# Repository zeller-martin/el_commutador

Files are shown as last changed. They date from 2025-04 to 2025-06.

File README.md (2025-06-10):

# el_commutador

a simple design for an active coaxial commutator with SMA connectors. used for tangle-free freely-moving neuronal recordings in small animals using ulca miniscopes or neuropixels probes. this design mainly differs from the design sold in the open ephys store in the follwowing aspects:
* mechanical parts and electronic controller are separate devices and connected with a cable
* use of a hollow-shaft stepper instead of a gear system decreases mechanical complexity and size of the device
* more simplistic and lower-priced design, but without any housing

# assembling the commutator

the file 'bom.xlsx' contains all necessary components. the file 'assembly.pdf' outlines the assembly of the hardware. the total cost of all components for a single commutator is ca. 300 euros.

# running the commutator

load the script 'motor_teensy.ino' onto the teensy 4.0 using arduino software with teensyduino software. the file 'el_commutador.py' contains the function 'run_commutator' to launch a GUI instance for a commutator. for now we feed real-time head direction information into the system by reading the head orientation .csv-file as it is written by the miniscope recording software. in the future other sources of head direction data can be implemented to be fed in the GUI. manual operation is also possible.

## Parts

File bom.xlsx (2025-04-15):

Description | Manufacturer | Part # | Amount
SMA coaxial slip ring | Jinpat | LPHF-01A | 1
Hex standoff with internal and external thread, M3 x 25mm | generic |  | 4
Hex standoff with internal and external thread, M3 x 5mm | generic |  | 4
Cap screw M3 x 8mm | generic |  | 4
Washer M3 | generic |  | 4
Coaxial cable assembly, Male SMA to Female SMA 100mm | RS components | 794-2914 | 1
Hollow shaft stepper motor | Nanotec | ST4118M1804-L | 1
Pin header 4x1 for stepper connection | JST | B4B-XH-A | 1
4 pin connector for stepper connection | Molex | 26013115 | 2
2m cable for stepper connection | Molex | 2451350420 | 1
Teensy 4.0 with headers | PJRC |  | 1
TMC2208 stepper driver with leads | BIGTREETECH | BIQU-ZZB000294 | 1
100 Ohms SMD resistor (footprint 2010) | generic |  | 1
3mm LED | generic |  | 1
DC barrel jack 2.1 mm | Wuerth Electronic | 694106301002 (or similar) | 1
14 pin header socket | Molex | 90147-1114 | 2
8 pin header socket | Molex | 90147-1108 | 2
circ_cap | 3D print from this repository |  | 1
hex_cap | 3D print from this repository |  | 1
commut_plate | from this repository, send to PCB fab (e.g. Aisler in Europe) |  | 1
controller_pcb | from this repository, send to PCB fab (e.g. Aisler in Europe) |  | 1
USB A to USB micro cable | generic |  | 1
DC power adapter, 12V, 2.A | XP power | VEL24US120-EU-JA (or similar) | 1
Plexiglass plate, 5mm thick, with cutouts | this repository, ideally commission at your instituions workshop |  | 1

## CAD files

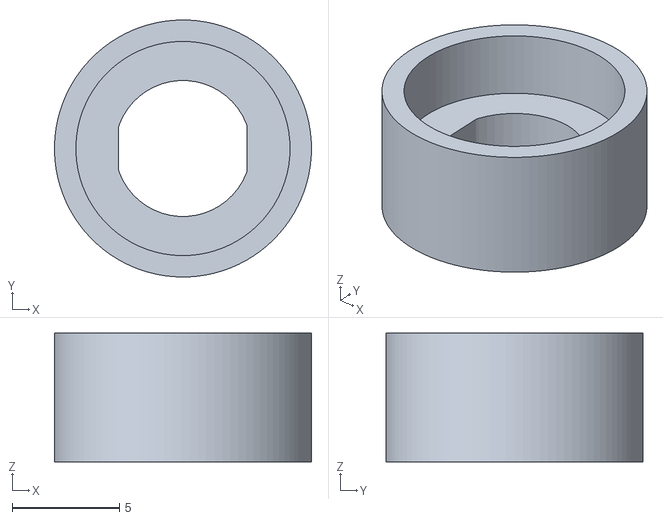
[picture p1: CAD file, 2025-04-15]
circ_cap.stl
12.0 x 12.0 x 6.00

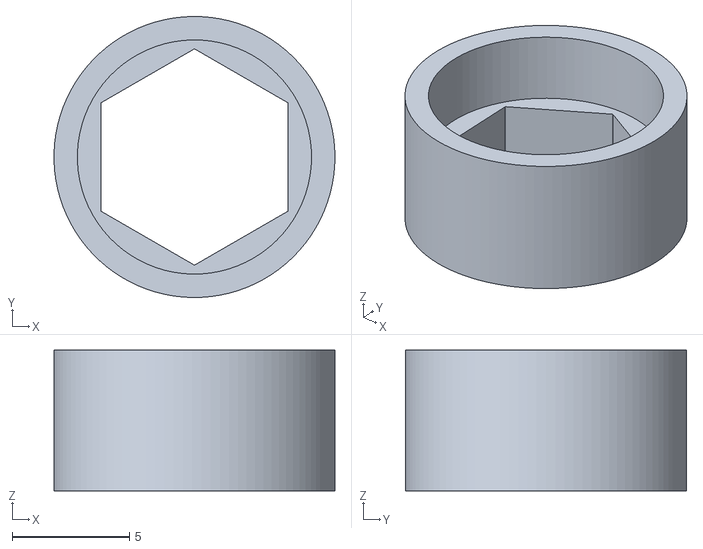
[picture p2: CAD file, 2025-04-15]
hex_cap.stl
12.0 x 12.0 x 6.00

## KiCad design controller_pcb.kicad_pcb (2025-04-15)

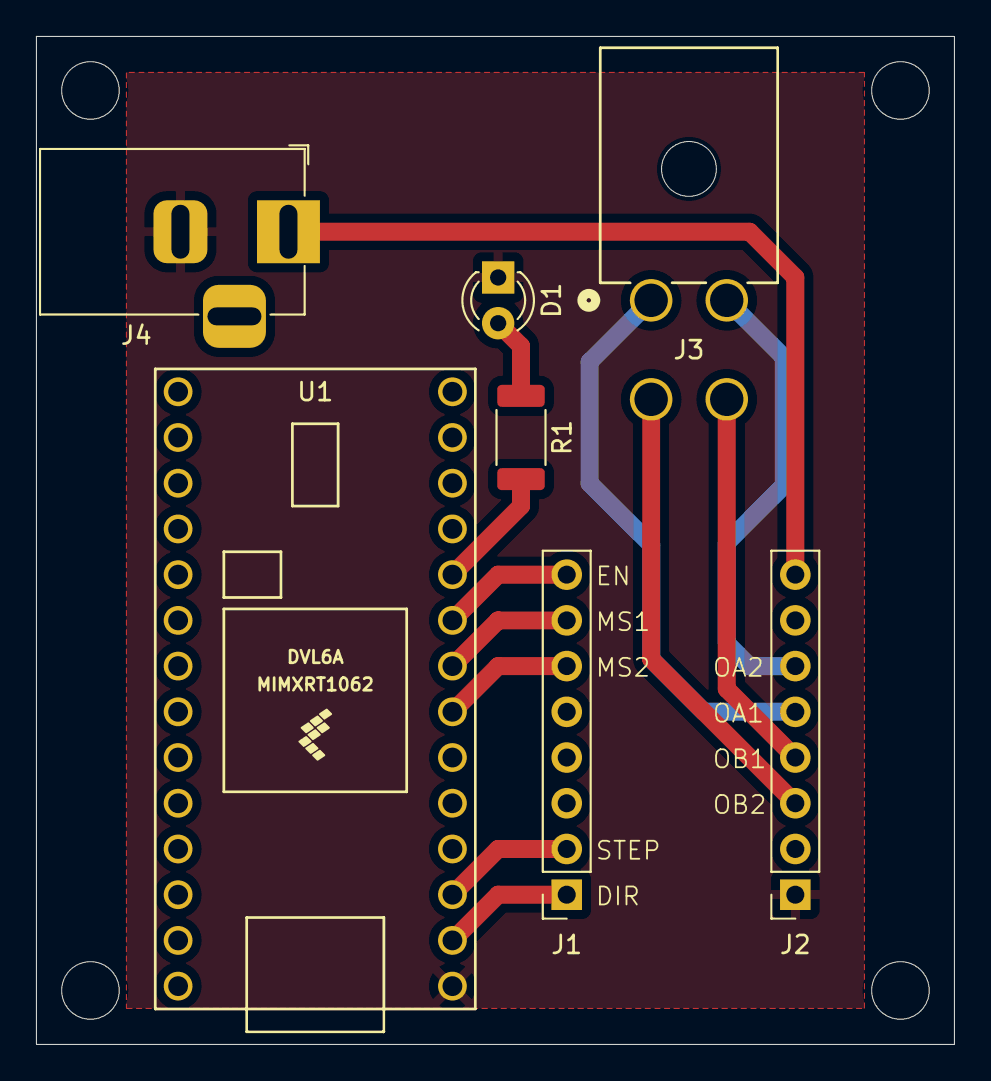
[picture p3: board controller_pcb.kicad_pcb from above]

Board: 2 copper layers, 51.0 x 56.0 mm, 7 parts (0 on the bottom side), 13 nets.

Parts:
D1: LED; LED_D3.0mm
J1, J2: Conn_01x08_Socket; PinSocket_1x08_P2.54mm_Vertical
J3: 26013115; CONN_5569-04A_MOL
J4: Barrel_Jack_MountingPin; BarrelJack_Horizontal
R1: R; R_2010_5025Metric
U1: Teensy4.0; Teensy40

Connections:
unnamed: D1.2 (A), R1.1
unnamed: D1.1 (K), J2.1, J4.2, U1.1 (GND)
unnamed: J1.1, U1.2 (0_RX1_CRX2_CS1)
unnamed: J1.2, U1.3 (1_TX1_CTX2_MISO1)
unnamed: J1.6, U1.7 (5_IN2)
unnamed: J1.7, U1.8 (6_OUT1D)
unnamed: J1.8, U1.9 (7_RX2_OUT1A)
unnamed: J2.3, J3.3
unnamed: J2.4, J3.4
unnamed: J2.5, J3.1
unnamed: J2.6, J3.2
unnamed: J2.8, J4.1
unnamed: R1.2, U1.10 (8_TX2_IN1)

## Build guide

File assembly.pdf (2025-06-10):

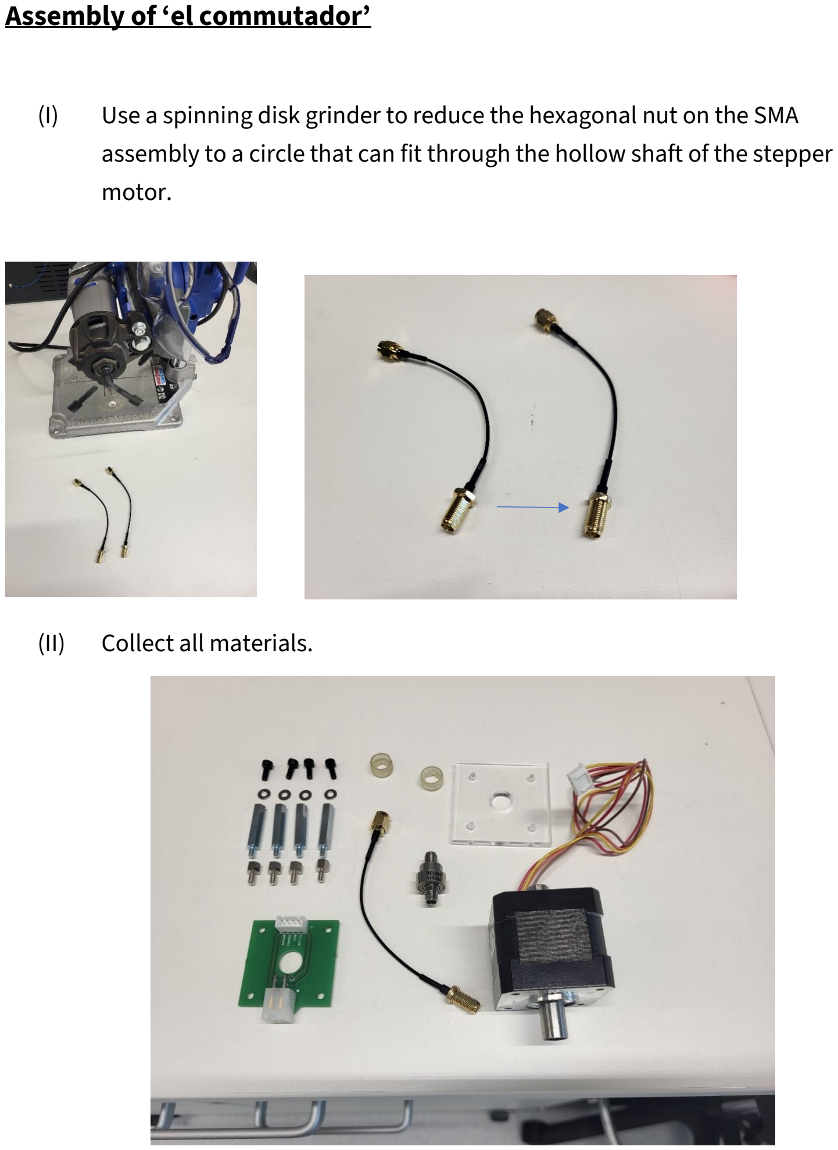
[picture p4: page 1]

Assembly of ‘el commutador’

(I) Use a spinning disk grinder to reduce the hexagonal nut on the SMA assembly to a circle that can fit through the hollow shaft of the stepper motor.

(II) Collect all materials.

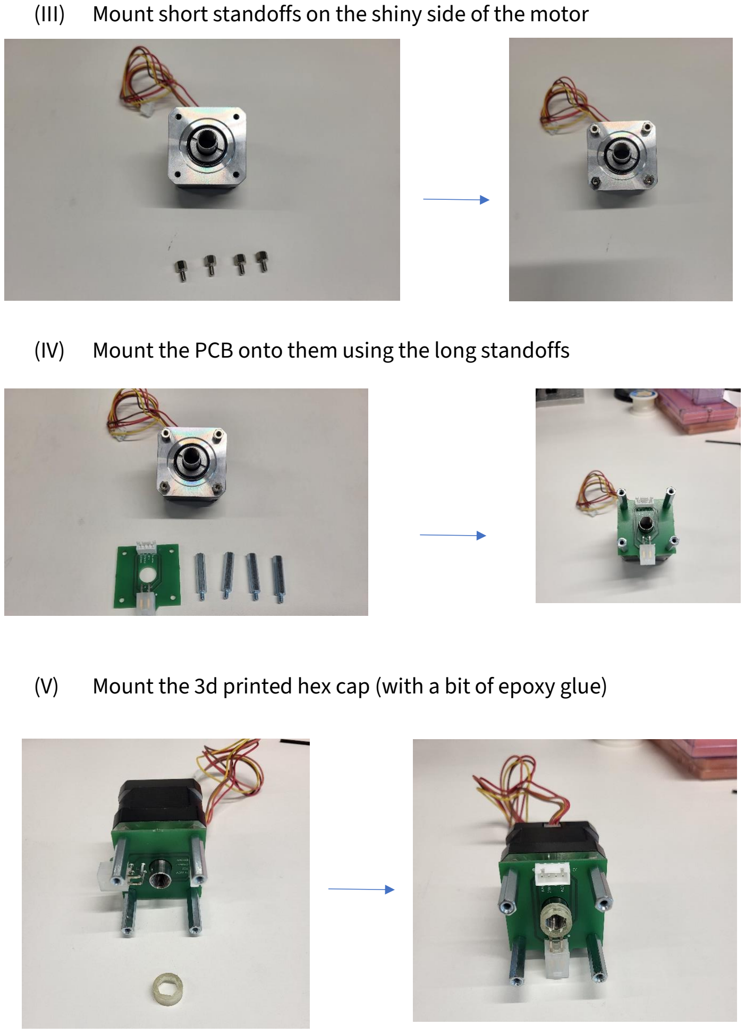
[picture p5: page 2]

(III) Mount short standoffs on the shiny side of the motor

(IV) Mount the PCB onto them using the long standoffs

(V) Mount the 3d printed hex cap (with a bit of epoxy glue)

(VI) Thread the SMA assembly through the hex cap and the hollow shaft, leading with the non-screw side

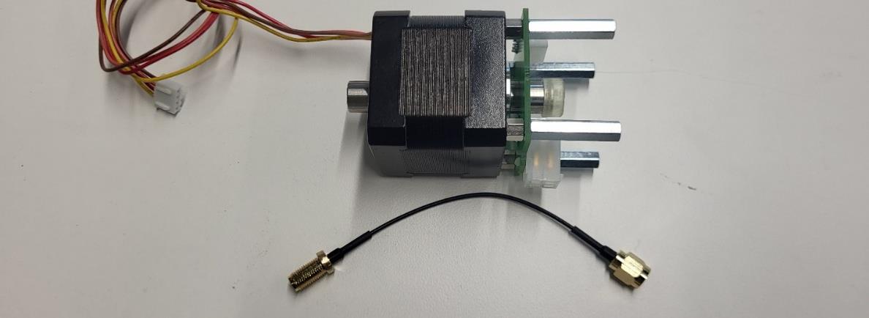
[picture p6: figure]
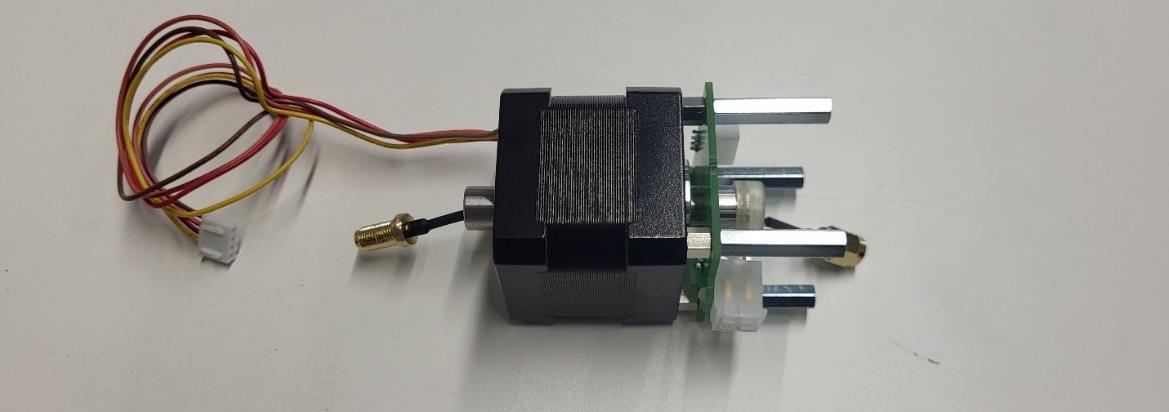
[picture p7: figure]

(VII) Connect the cable on the two sides with the circular cap and the slip ring.

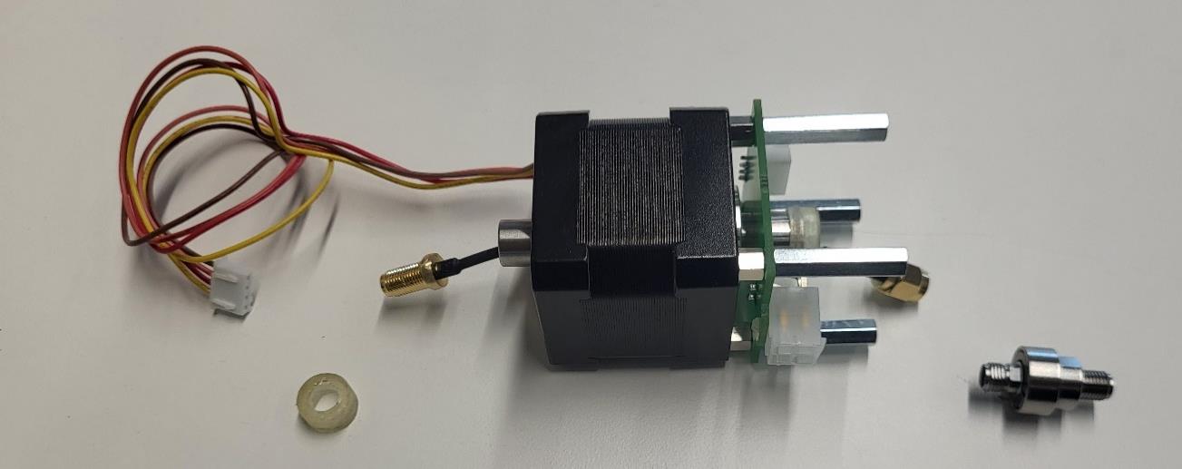
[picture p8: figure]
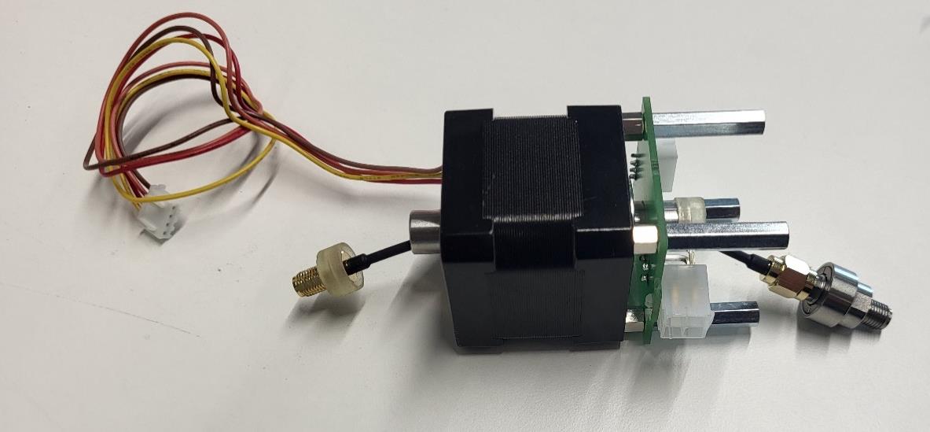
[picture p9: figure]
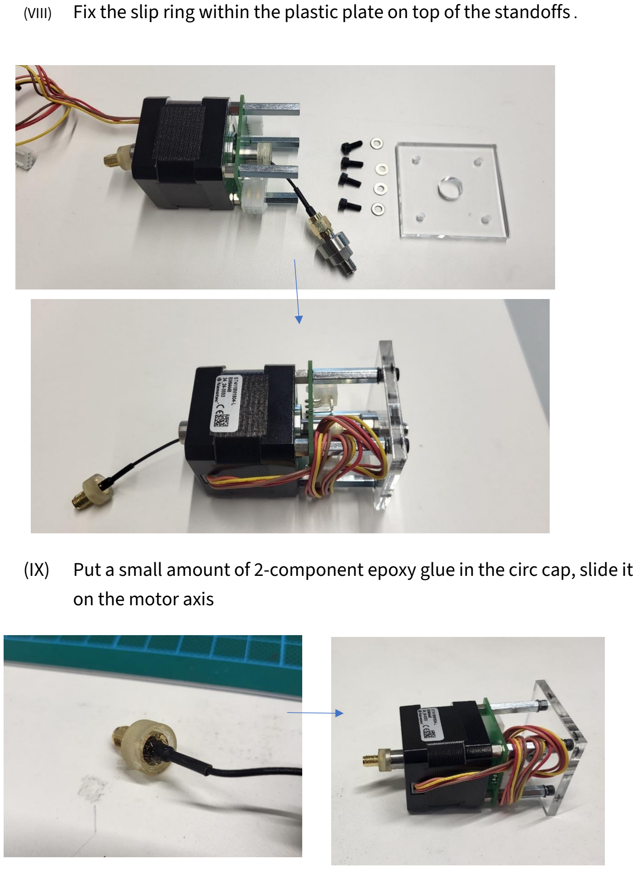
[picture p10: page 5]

(VIII) Fix the slip ring within the plastic plate on top of the standoffs .

(IX) Put a small amount of 2-component epoxy glue in the circ cap, slide it on the motor axis

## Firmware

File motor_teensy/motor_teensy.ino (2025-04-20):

// ------------------- Pin Definitions -------------------
#define stp         1   // Step pin for stepper driver
#define dir         0   // Direction pin
#define MS1         6   // Microstep control pin 1
#define MS2         5   // Microstep control pin 2
#define EN          7   // Enable pin
#define LED_DISABLE 8   // Optional LED for showing disabled state

#define MIN_SPEED_FAC 0.02  // Minimum speed factor for smooth deceleration

// ------------------- State Variables -------------------
long pos      = 0;        // Current motor position (in steps)
long target   = 0;        // Target position
long delta    = 0;        // Distance to move
long step_t   = 5000;     // Base step delay in microseconds
long _step_t  = step_t;   // Adjusted step delay for dynamic speed
long steps_per_turn = 200; // Steps per full rotation (200 or 3200 in microstep)

float fac     = 1;        // Speed scaling factor

// ------------------- Timing -------------------
elapsedMicros clock_time;
unsigned long next_off_time = 0;
unsigned long next_on_time  = 0;

// ------------------- Communication Buffer -------------------
byte send_arr[4]; // Used for sending 4-byte integers (position)

// ------------------- Flags -------------------
bool step_on   = false;
bool in_pause  = false;


// ------------------- Functions -------------------

// Parses a long integer from the serial buffer until 'X' is received
void assign_param(long int *param) {
  String received_string;
  char c;

  while (1) {
    if (Serial.available()) {
      c = Serial.read();
      if (c == 'X') {
        break;
      } else {
        received_string += c;
      }
    }
  }

  received_string.replace("\n", "");
  *param = received_string.toInt();
}

// Resets all stepper-related pins to default inactive states
void resetBEDPins() {
  digitalWrite(stp, LOW);
  digitalWrite(dir, LOW);
  digitalWrite(MS1, LOW);
  digitalWrite(MS2, LOW);
  digitalWrite(EN, HIGH);
}

// Enables or disables microstepping (sets steps_per_turn accordingly)
void activate_microstep(bool yes) {
  if (yes) {
    digitalWrite(MS1, HIGH);
    digitalWrite(MS2, HIGH);
    steps_per_turn = 3200;  // 1/16 microstepping
  } else {
    digitalWrite(MS1, LOW);
    digitalWrite(MS2, LOW);
    steps_per_turn = 200;   // Full step
  }
}

// Flash LED to enable assignment of serial port to physical device
void ping() {
  for (byte i = 0; i < 10; ++i) {
    digitalWrite(LED_DISABLE, HIGH);
    delay(50);
    digitalWrite(LED_DISABLE, LOW);
    delay(50);
  }
}


// ------------------- Setup -------------------

void setup() {
  // Configure pins
  pinMode(LED_BUILTIN, OUTPUT);
  pinMode(stp, OUTPUT);
  pinMode(dir, OUTPUT);
  pinMode(MS1, OUTPUT);
  pinMode(MS2, OUTPUT);
  pinMode(EN, OUTPUT);
  pinMode(LED_DISABLE, OUTPUT);

  resetBEDPins();

  // Initialize serial communication
  Serial.begin(115200);

  // Enable the stepper driver
  digitalWrite(EN, LOW);

  // Enable microstepping by default
  activate_microstep(true);
}


// ------------------- Main Loop -------------------

void loop() {
  // --- Handle Serial Commands ---
  if (Serial.available()) {
    byte recv_byte = Serial.read();

    switch (recv_byte) {
      case 'P': assign_param(&target); break;       // Set new target position
      case 'F': ping(); break;                      // Flash status LED
      case 'R':                                     // Reset state and enable microstep
        pos = 0;
        target = 0;
        clock_time = 0;
        next_on_time = 0;
        next_off_time = 0;
        activate_microstep(true);
        in_pause = false;
        break;
      case 'T': assign_param(&step_t); break;       // Set base step time
      case 'M': activate_microstep(true); break;    // Enable microstepping
      case 'N': activate_microstep(false); break;   // Disable microstepping
      case 'S':                                     // Stop motor
        in_pause = true;
        digitalWrite(LED_DISABLE, HIGH);
        break;
      case 'G':                                     // Resume motor
        in_pause = false;
        digitalWrite(LED_DISABLE, LOW);
        break;
      case 'Q':                                     // Send current position as 4 bytes
        send_arr[0] =  pos        & 0xFF;
        send_arr[1] = (pos >>  8) & 0xFF;
        send_arr[2] = (pos >> 16) & 0xFF;
        send_arr[3] = (pos >> 24) & 0xFF;
        Serial.write(send_arr, 4);
        break;
    }
  }

  // --- Determine Direction and Distance to Target ---
  if (pos > target) {
    digitalWrite(dir, HIGH);     // Set direction backward
    delta = pos - target;
  } else {
    digitalWrite(dir, LOW);      // Set direction forward
    delta = target - pos;
  }

  // --- Dynamically Adjust Step Time Based on Distance ---
  if (delta > (steps_per_turn / 8)) {
    _step_t = step_t;
  } else {
    fac = float(step_t) * (1 / (((1 - MIN_SPEED_FAC) * (float(delta) / (steps_per_turn / 8))) + MIN_SPEED_FAC));
    _step_t = long(fac);
  }

  // --- Step Motor if Not Paused ---
  if (!in_pause) {
    if (pos != target) {
      digitalWrite(EN, LOW);  // Ensure driver is enabled

      if (!step_on && clock_time >= next_on_time) {
        digitalWrite(stp, HIGH);            // Start step pulse
        digitalWrite(LED_BUILTIN, HIGH);
        step_on = true;
        next_off_time = _step_t;
        clock_time = 0;
      } else if (step_on && clock_time >= next_off_time) {
        digitalWrite(stp, LOW);             // End step pulse
        digitalWrite(LED_BUILTIN, LOW);
        step_on = false;
        next_on_time = _step_t;
        clock_time = 0;

        // Update position
        if (digitalRead(dir)) {
          pos--;
        } else {
          pos++;
        }
      }
    } else {
      // Hold current state if target reached
      digitalWrite(stp, LOW);
      step_on = false;
      digitalWrite(LED_BUILTIN, LOW);
    }
  }
}

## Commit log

2025-04-15 add files for commutator construction
    [bom.xlsx, circ_cap.stl, commut_plate.kicad_pcb, controller_pcb.kicad_pcb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]
2025-04-15 added specifications for plexiglass plate
    [bom.xlsx]
2025-04-15 update bon
    [bom.xlsx]
2025-04-20 remove unused pin
2025-06-10 added assembly manual
